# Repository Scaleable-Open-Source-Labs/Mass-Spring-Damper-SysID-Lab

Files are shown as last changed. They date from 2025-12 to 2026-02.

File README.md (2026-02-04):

This is the source repo for the Mass Spring Damper SysID Lab - if you are looking for usage instructions, head to the [user-guide](https://scaleable-open-source-labs.github.io/mass-spring-damper-sysid-lab.html)

---

A low-cost dynamics lab that allows students to perform System Identification on a real Mass-Spring-Damper system.

*Designed by Michael Ruppe for Monash University in partnership with MathWorks®*

## Bill of Materials

### Mechanical Components
- 12 x [SC M3X8 304](https://nhtb.com.au/SC%20M3X8%20304.html)
-  2 x [SC M3X16 304](https://nhtb.com.au/SC%20M3X16%20304.html)
-  2 x [Steel Extension Spring, 27.2 mm x 4 mm OD](https://au.rs-online.com/web/p/extension-springs/0751663)

### Enclosure & Printed Parts
*The printed case and acrylic lid were modeled in OnShape. You can inspect and fork your own copy of the [OnShape project](https://cad.onshape.com/documents/9c2f20cdbdc0ad1f01a0b817/w/781d57bc81f27fd7521e8d8c/e/460a2fa13b5ff0fbf298da99?renderMode=0&uiState=6969b017818b6df756886df9)*

- Case
- Guide Rails
- Lid

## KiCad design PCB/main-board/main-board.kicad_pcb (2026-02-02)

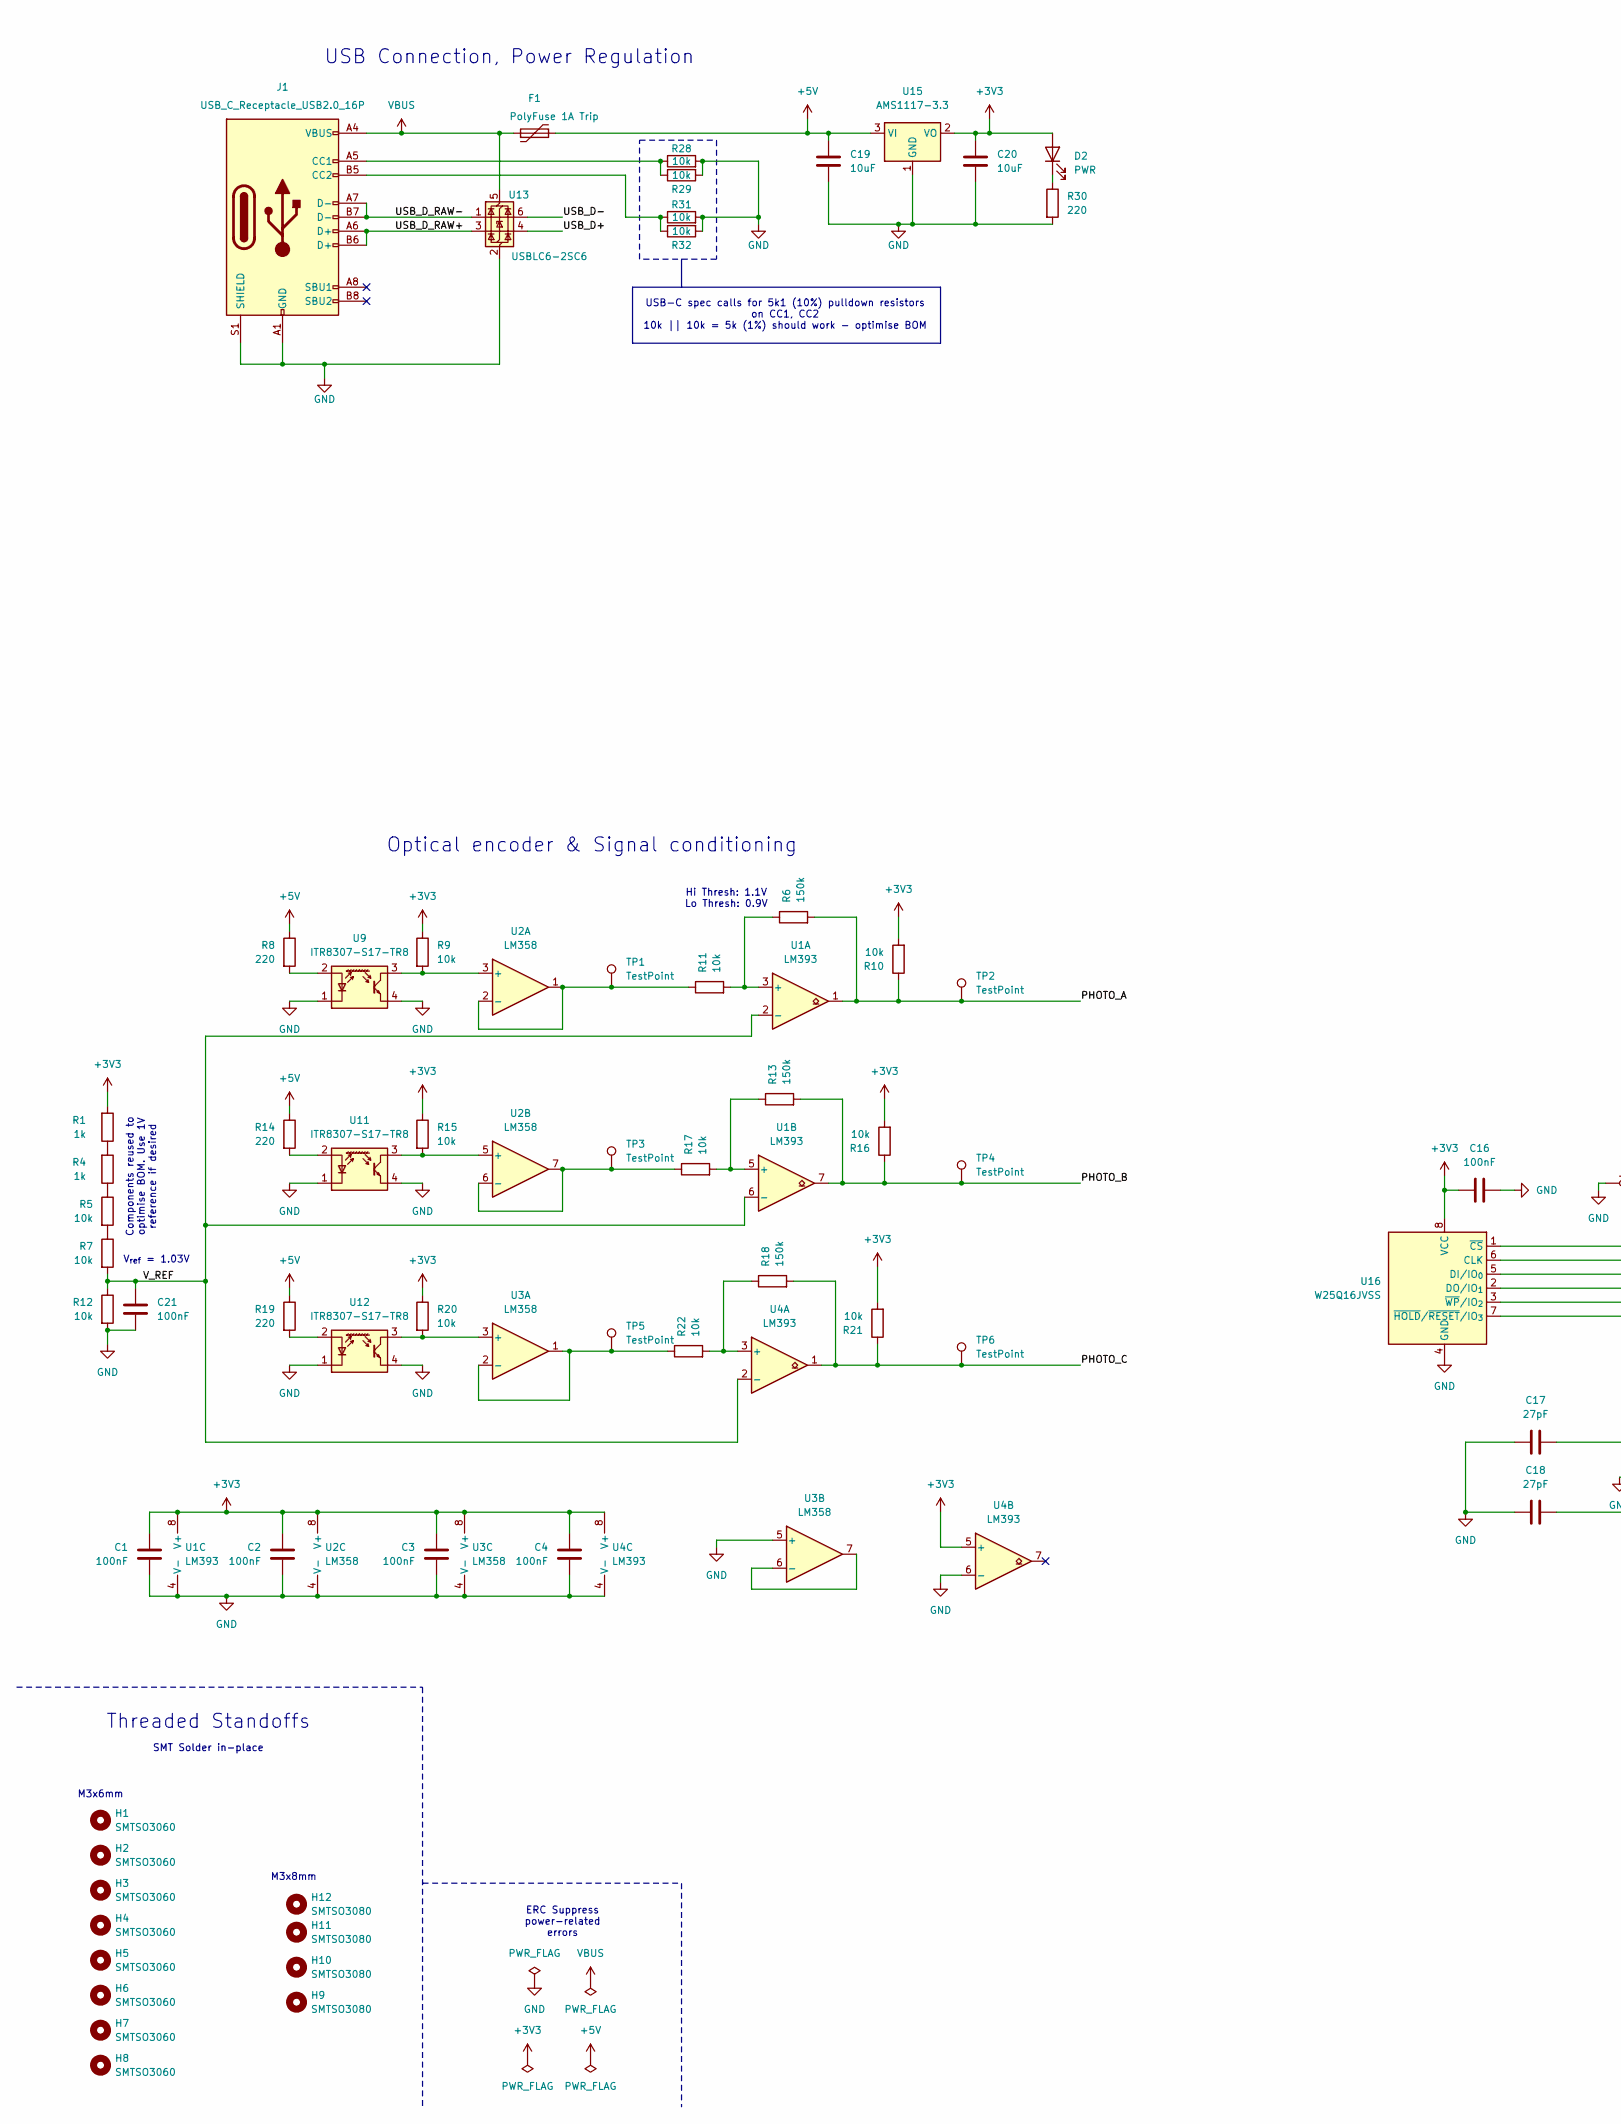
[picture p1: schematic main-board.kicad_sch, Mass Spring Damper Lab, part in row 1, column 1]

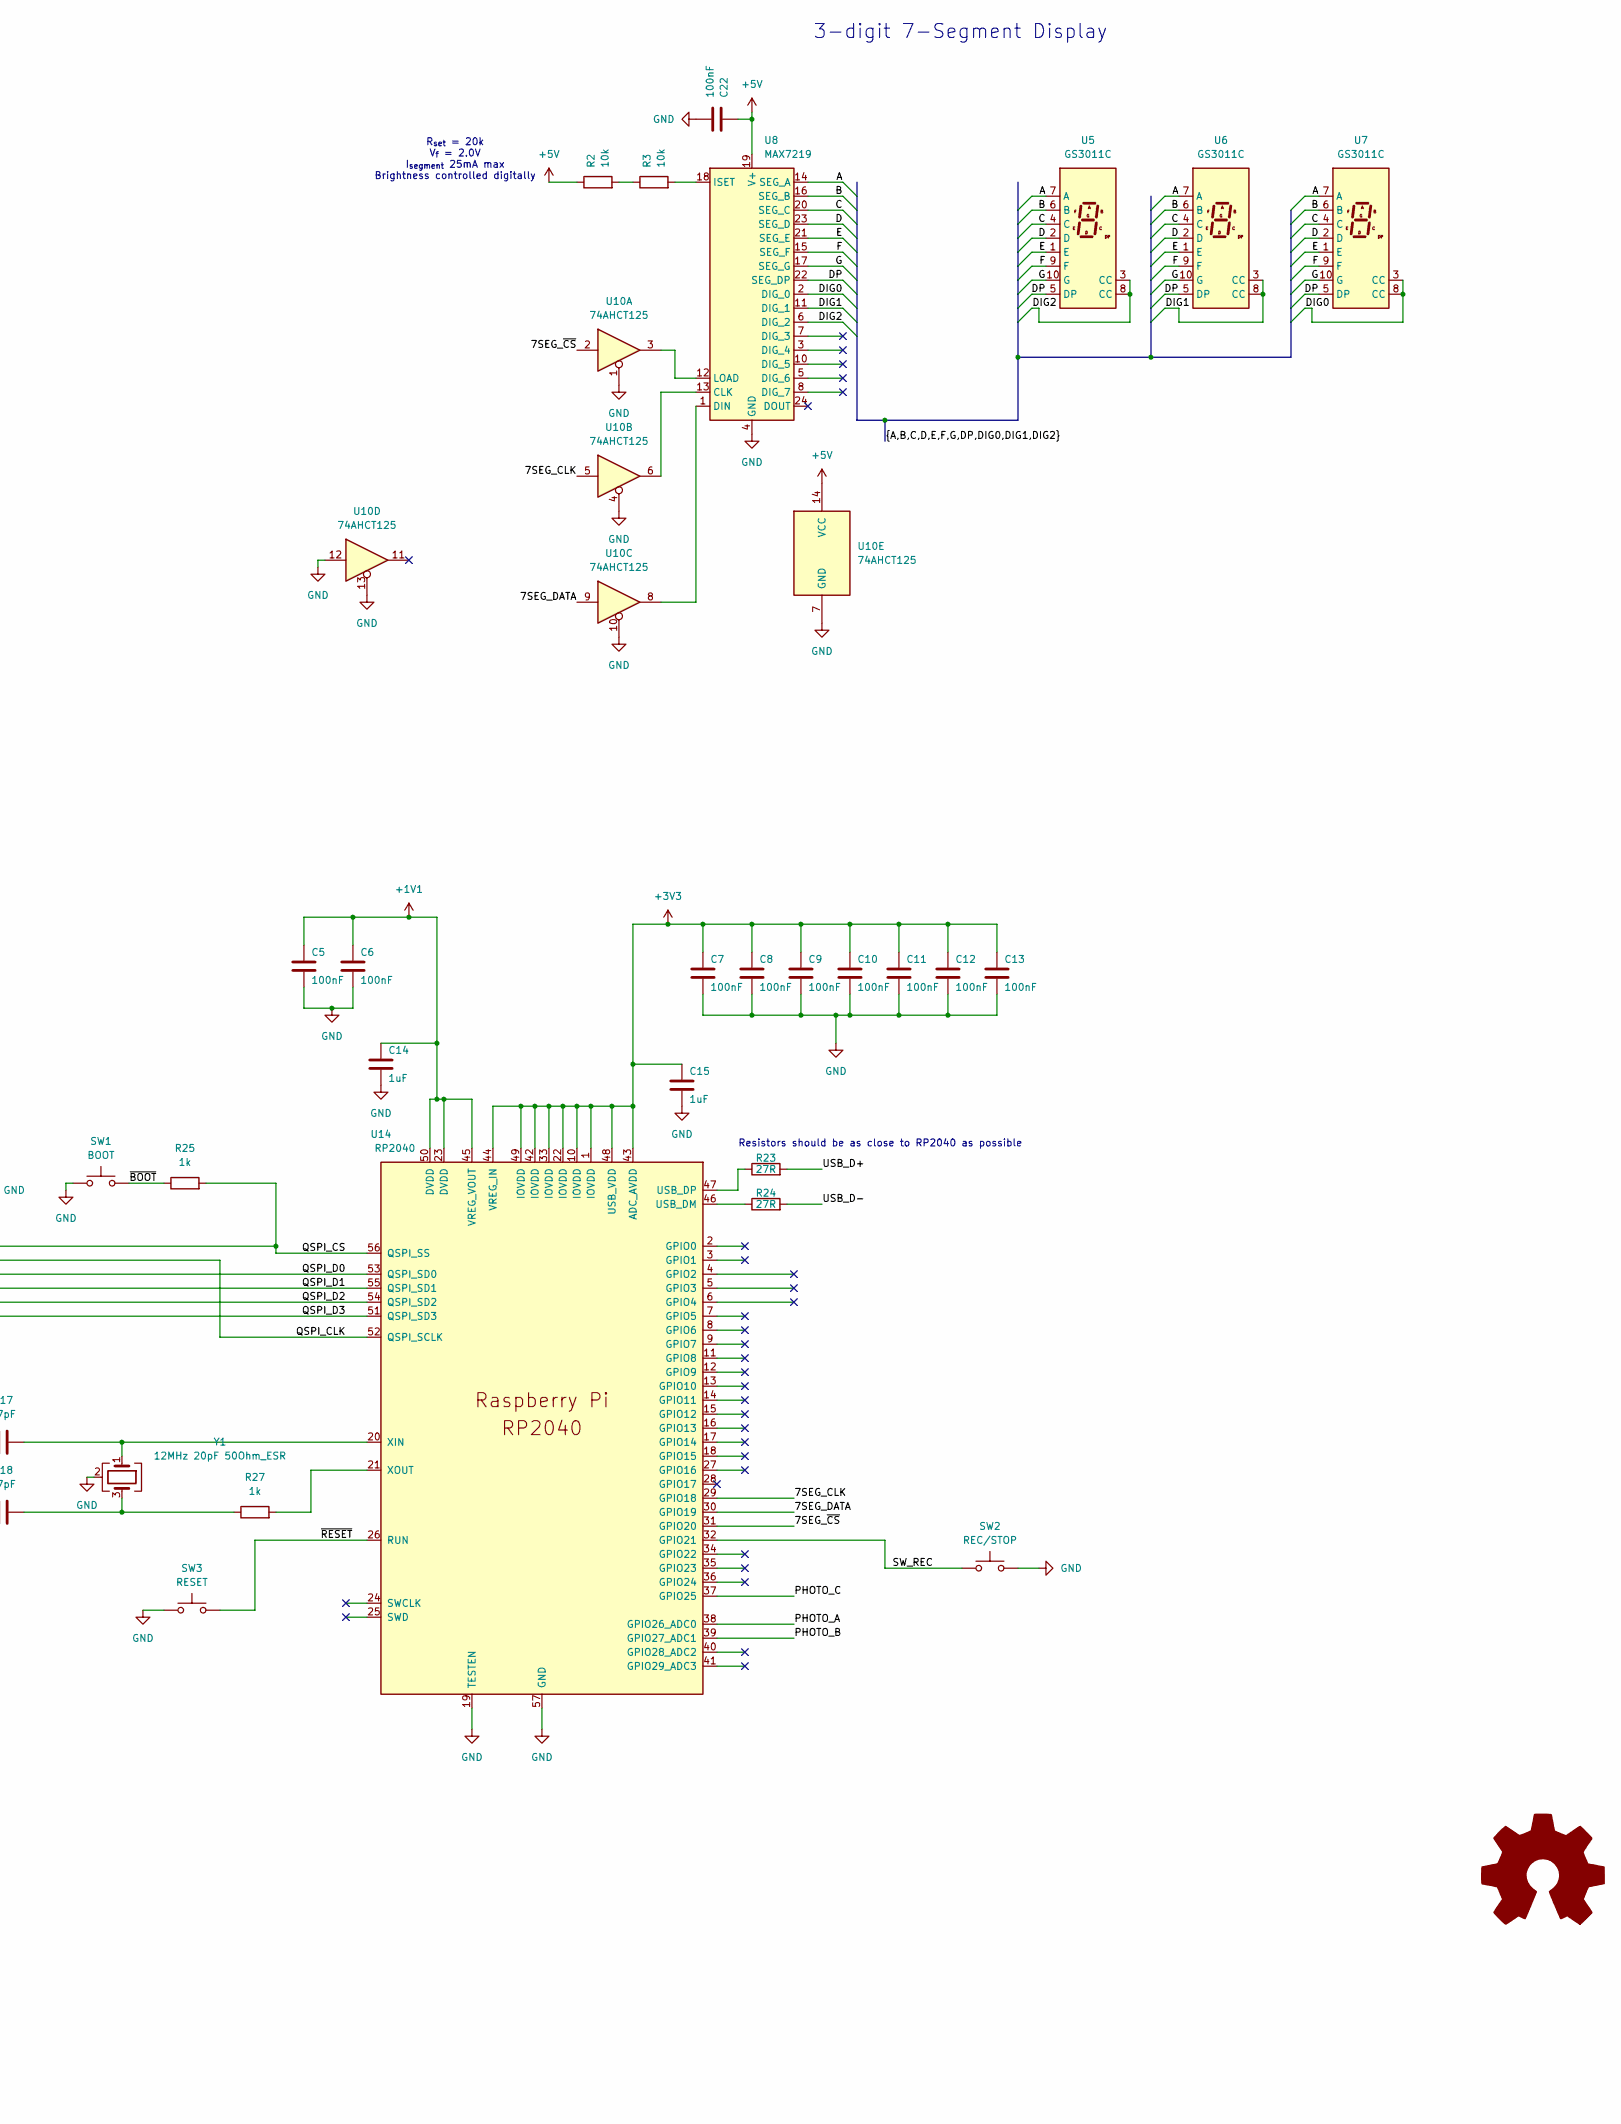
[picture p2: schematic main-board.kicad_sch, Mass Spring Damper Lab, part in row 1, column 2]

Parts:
C1, C2, C3, C4, C5, C6, C7, C8, C9, C10, C11, C12, C13, C16, C21, C22: 100nF; C_0603_1608Metric; LCSC Part # C14663
C14, C15: 1uF; C_0603_1608Metric; LCSC Part # C15849
C17, C18: 27pF; C_0603_1608Metric; LCSC Part # C1656
C19, C20: 10uF; C_0603_1608Metric; LCSC Part # C19702
D2: PWR; LED_0603_1608Metric; LCSC Part # C965807
F1: PolyFuse 1A Trip; R_1206_3216Metric; LCSC Part # C720075
H1, H2, H3, H4, H5, H6, H7, H8: SMTSO3060; MountingHole_SMTSO3060_3.2mm_M3; LCSC Part # C2915637
H9, H10, H11, H12: SMTSO3080; MountingHole_SMTSO3080_3.2mm_M3; LCSC Part # C2916369
J1: USB_C_Receptacle_USB2.0_16P; USB_C_Receptacle_HCTL_HC-TYPE-C-16P-01A; LCSC Part # C2894897
R1, R4, R25, R27: 1k; R_0603_1608Metric; LCSC Part # C21190
R2, R3, R5, R7, R9, R10, R11, R12, R15, R16, R17, R20, R21, R22, R28, R29, R31, R32: 10k; R_0603_1608Metric; LCSC Part # C25804
R6, R13, R18: 150k; R_0603_1608Metric; LCSC Part # C22807
R8, R14, R19, R30: 220; R_0603_1608Metric; LCSC Part # C22962
R23, R24: 27R; R_0603_1608Metric; LCSC Part # C25190
SW1: BOOT; SW_Push_1P1T_NO_E-Switch_TL3301NxxxxxG; LCSC Part # C455109
SW2: REC/STOP; SW_SPST_Omron_B3F-40xx; LCSC Part # C84931
SW3: RESET; SW_SPST_Omron_B3F-40xx; LCSC Part # C84931
TP1, TP2, TP3, TP4, TP5, TP6: TestPoint; TestPoint_Pad_D1.5mm
U1, U4: LM393; SOIC-8_3.9x4.9mm_P1.27mm; LCSC Part # C32901
U2, U3: LM358; SOIC-8_3.9x4.9mm_P1.27mm; LCSC Part # C9418
U5, U6, U7: GS3011C; GS3011; LCSC Part # C22462660
U8: MAX7219; SOIC-24W_7.5x15.4mm_P1.27mm; LCSC Part # C49443603
U9, U11, U12: ITR8307-S17-TR8; Everlight_ITR1201SR10AR; LCSC Part # C81632
U10: 74AHCT125; SOIC-14_3.9x8.7mm_P1.27mm; LCSC Part # C5962
U13: USBLC6-2SC6; SOT-23-6; LCSC Part # C2687116
U14: RP2040; RP2040-QFN-56; PARTREV 1.6.1; LCSC Part # C2040
U15: AMS1117-3.3; SOT-223-3_TabPin2; LCSC Part # C6186
U16: W25Q16JVSS; SOIC-8_5.3x5.3mm_P1.27mm; LCSC Part # C82317
Y1: 12MHz 20pF 50Ohm_ESR; Crystal_SMD_3225-4Pin_3.2x2.5mm; LCSC Part # C133334

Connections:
+1V1: C5.1, C6.1, C14.1, U14.23 (DVDD), U14.45 (VREG_VOUT), U14.50 (DVDD)
+3V3: C1.1, C2.1, C3.1, C4.1, C7.1, C8.1, C9.1, C10.1, C11.1, C12.1, C13.1, C15.1, C16.1, C20.1, D2.2 (A), R1.2, R9.1, R10.2, R15.1, R16.2, R20.1, R21.2, U1.8 (V+), U2.8 (V+), U3.8 (V+), U4.5 (+), U4.8 (V+), U14.1 (IOVDD), U14.10 (IOVDD), U14.22 (IOVDD), U14.33 (IOVDD), U14.42 (IOVDD), U14.43 (ADC_AVDD), U14.44 (VREG_IN), U14.48 (USB_VDD), U14.49 (IOVDD), U15.2 (VO), U16.8 (VCC)
+5V: C19.1, C22.1, F1.2, R2.1, R8.1, R14.1, R19.1, U8.19 (V+), U10.14 (VCC), U15.3 (VI)
/7SEG_CLK: U10.5, U14.29 (GPIO18)
/7SEG_DATA: U10.9, U14.30 (GPIO19)
/7SEG_~CS: U10.2, U14.31 (GPIO20)
/A: U5.7 (A), U6.7 (A), U7.7 (A), U8.14 (SEG_A)
/B: U5.6 (B), U6.6 (B), U7.6 (B), U8.16 (SEG_B)
/C: U5.4 (C), U6.4 (C), U7.4 (C), U8.20 (SEG_C)
/D: U5.2 (D), U6.2 (D), U7.2 (D), U8.23 (SEG_D)
/DIG0: U7.3 (CC), U7.8 (CC), U8.2 (DIG_0)
/DIG1: U6.3 (CC), U6.8 (CC), U8.11 (DIG_1)
/DIG2: U5.3 (CC), U5.8 (CC), U8.6 (DIG_2)
/DP: U5.5 (DP), U6.5 (DP), U7.5 (DP), U8.22 (SEG_DP)
/E: U5.1 (E), U6.1 (E), U7.1 (E), U8.21 (SEG_E)
/F: U5.9 (F), U6.9 (F), U7.9 (F), U8.15 (SEG_F)
/G: U5.10 (G), U6.10 (G), U7.10 (G), U8.17 (SEG_G)
/PHOTO_A: R6.2, R10.1, TP2.1, U1.1, U14.38 (GPIO26_ADC0)
/PHOTO_B: R13.2, R16.1, TP4.1, U1.7, U14.39 (GPIO27_ADC1)
/PHOTO_C: R18.2, R21.1, TP6.1, U4.1, U14.37 (GPIO25)
/QSPI_CLK: U14.52 (QSPI_SCLK), U16.6 (CLK)
/QSPI_CS: R25.2, U14.56 (QSPI_SS), U16.1 (~CS)
/QSPI_D0: U14.53 (QSPI_SD0), U16.5 (DI/IO_{0})
/QSPI_D1: U14.55 (QSPI_SD1), U16.2 (DO/IO_{1})
/QSPI_D2: U14.54 (QSPI_SD2), U16.3 (~WP/IO_{2})
/QSPI_D3: U14.51 (QSPI_SD3), U16.7 (~HOLD/~RESET/IO_{3})
/SW_REC: SW2.1, U14.32 (GPIO21)
/USB_D+: R23.2, U13.4 (I/O2)
/USB_D-: R24.2, U13.6 (I/O1)
/USB_D_RAW+: J1.A6 (D+), J1.B6 (D+), U13.3 (I/O2)
/USB_D_RAW-: J1.A7 (D-), J1.B7 (D-), U13.1 (I/O1)
/V_REF: C21.1, R7.2, R12.1, U1.2 (-), U1.6 (-), U4.2 (-)
/~BOOT: R25.1, SW1.1
/~RESET: SW3.1, U14.26 (RUN)
GND: C1.2, C2.2, C3.2, C4.2, C5.2, C6.2, C7.2, C8.2, C9.2, C10.2, C11.2, C12.2, C13.2, C14.2, C15.2, C16.2, C17.1, C18.1, C19.2, C20.2, C21.2, C22.2, J1.A1 (GND), J1.A12 (GND), J1.B1 (GND), J1.B12 (GND), J1.S1 (SHIELD), R12.2, R28.2, R29.2, R30.2, R31.2, R32.2, SW1.2, SW2.2, SW3.2, U1.4 (V-), U2.4 (V-), U3.4 (V-), U3.5 (+), U4.4 (V-), U4.6 (-), U8.4 (GND), U8.9 (GND), U9.1 (K), U9.4, U10.1, U10.4, U10.7 (GND), U10.10, U10.12, U10.13, U11.1 (K), U11.4, U12.1 (K), U12.4, U13.2 (GND), U14.19 (TESTEN), U14.57 (GND), U15.1 (GND), U16.4 (GND), Y1.2 (G), Y1.4 (G)
unnamed: C18.2, R27.1, Y1.3
unnamed: D2.1 (K), R30.1
unnamed: J1.A5 (CC1), R28.1, R29.1
unnamed: J1.B5 (CC2), R31.1, R32.1
unnamed: R1.1, R4.2
unnamed: R2.2, R3.1
unnamed: R4.1, R5.1
unnamed: R5.2, R7.1
unnamed: R6.1, R11.2, U1.3 (+)
unnamed: R13.1, R17.2, U1.5 (+)
unnamed: R9.2, U2.3 (+), U9.3
unnamed: R11.1, TP1.1, U2.1, U2.2 (-)
unnamed: R15.2, U2.5 (+), U11.3
unnamed: R17.1, TP3.1, U2.6 (-), U2.7
unnamed: R20.2, U3.3 (+), U12.3
unnamed: R22.1, TP5.1, U3.1, U3.2 (-)
unnamed: U3.6 (-), U3.7
unnamed: R18.1, R22.2, U4.3 (+)
unnamed: U8.13 (CLK), U10.6
unnamed: U8.1 (DIN), U10.8
unnamed: R3.2, U8.18 (ISET)
unnamed: U8.12 (LOAD), U10.3
unnamed: R8.2, U9.2 (A)
unnamed: R14.2, U11.2 (A)
unnamed: R19.2, U12.2 (A)
unnamed: R24.1, U14.46 (USB_DM)
unnamed: R23.1, U14.47 (USB_DP)
unnamed: C17.2, U14.20 (XIN), Y1.1
unnamed: R27.2, U14.21 (XOUT)
VBUS: F1.1, J1.A4 (VBUS), J1.A9 (VBUS), J1.B4 (VBUS), J1.B9 (VBUS), U13.5 (VBUS)

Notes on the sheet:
USB-C spec calls for 5k1 (10%) pulldown resistors on CC1, CC2 10k || 10k = 5k (1%) should work - optimise BOM
M3x6mm
Resistors should be as close to RP2040 as possible
Hi Thresh: 1.1V Lo Thresh: 0.9V
3-digit 7-Segment Display
Threaded Standoffs
Components reused to optimise BOM. Use 1V reference if desired
USB Connection, Power Regulation
ERC Suppress power-related errors
SMT Solder in-place
R_{set} = 20k V_{f} = 2.0V I_{segment} 25mA max Brightness controlled digitally
Optical encoder & Signal conditioning
M3x8mm
V_{ref} = 1.03V

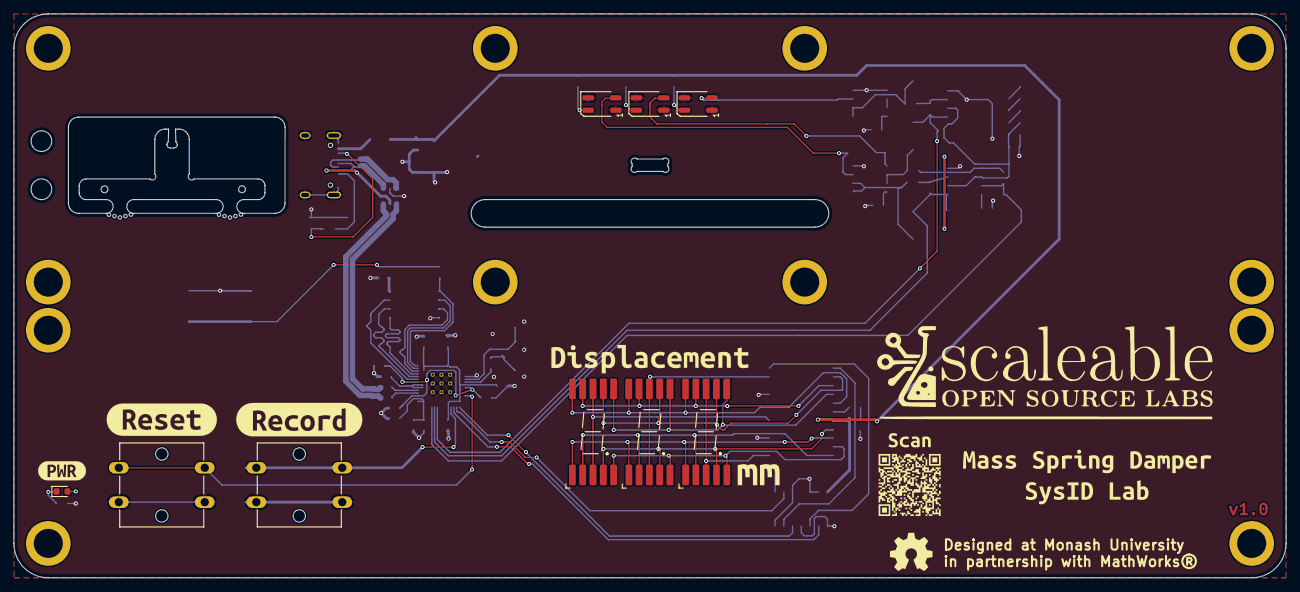
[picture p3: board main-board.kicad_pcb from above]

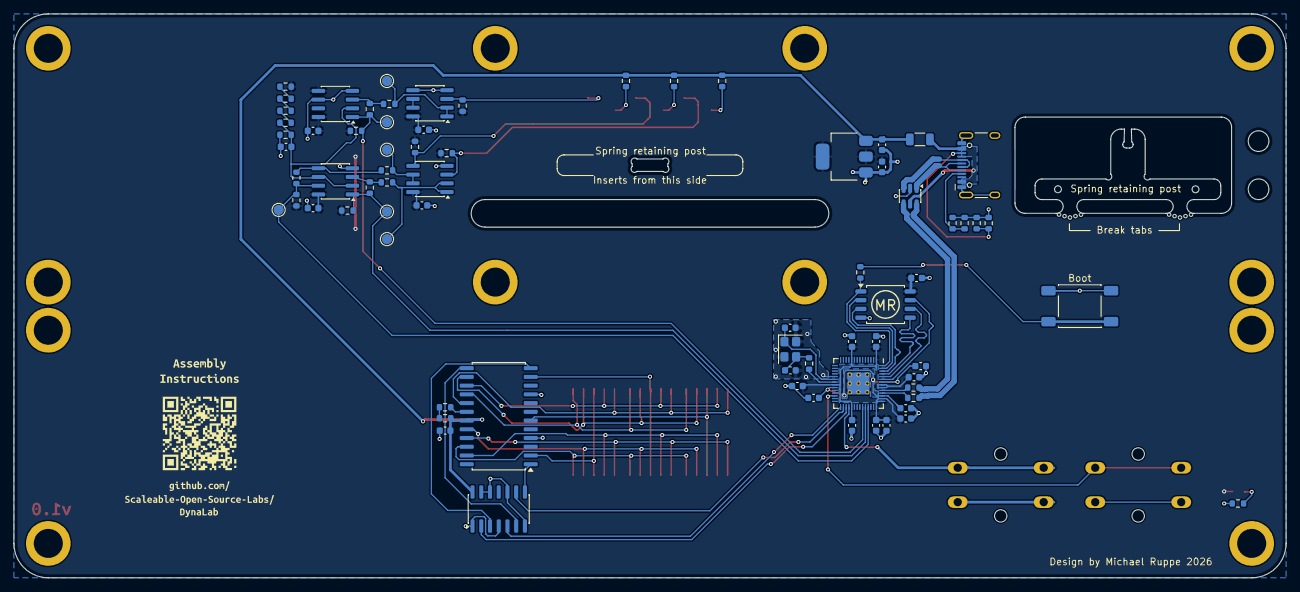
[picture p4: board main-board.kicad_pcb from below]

Board: 2 copper layers, 185.0 x 82.0 mm, 110 parts (86 on the bottom side), 65 nets.

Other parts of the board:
kibuzzard-6930AF86: G***; kibuzzard-6930AF86
kibuzzard-6930AFAB: G***; kibuzzard-6930AFAB
kibuzzard-69645CED: G***; kibuzzard-69645CED
kibuzzard-697836DA: G***; kibuzzard-697836DA
kibuzzard-697848C9: G***; kibuzzard-697848C9
kibuzzard-6964435B: G***; kibuzzard-6964435B
kibuzzard-6978203B: G***; kibuzzard-6978203B
kibuzzard-6978204E: G***; kibuzzard-6978204E
kibuzzard-6978363D: G***; kibuzzard-6978363D
kibuzzard-6978422B: G***; kibuzzard-6978422B
kibuzzard-69310180: G***; kibuzzard-69310180
kibuzzard-69310240: G***; kibuzzard-69310240
kibuzzard-69783696: G***; kibuzzard-69783696
kibuzzard-69784254: G***; kibuzzard-69784254
mousebite1, mousebite2: VAL**; mouse-bite-2mm-4mm-single-sided

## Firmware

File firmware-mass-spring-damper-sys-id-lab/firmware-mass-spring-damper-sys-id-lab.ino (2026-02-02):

#define VERSION_MAJOR 0
#define VERSION_MINOR 1

// Create version string using preprocessor stringification
#define STRINGIFY(x) #x
#define TOSTRING(x) STRINGIFY(x)
#define VERSION_STRING TOSTRING(VERSION_MAJOR) "." TOSTRING(VERSION_MINOR)

#include <Arduino.h>
#include "Adafruit_TinyUSB.h"
#include "ramdisk.h"
#include "gpio.h"
#include "LedControl.h"

LedControl lc = LedControl(19, 18, 20, 1);

#define CAPTURE_TIMEOUT_MS 5000  // maximum possible recording duration
#define MOTION_TIMEOUT_MS 500    // timeout when mass has stopped moving
#define USB_DETACH_DELAY_MS 10
#define SERIAL_WAIT_MS 100
#define POST_CAPTURE_DELAY_MS 1000

// Volatile variables shared between ISR and main loop
volatile bool stateChanged = false;
volatile int positionCounter = 0;

// State tracking
uint8_t currentState = 0;
uint8_t previousState = 0;

unsigned long timestamp = 0;

Adafruit_USBD_MSC usb_msc;

// Data collection structure
#define MAX_DATAPOINTS 5000
struct DataPoint {
  uint32_t millisecond;
  int displacement_mm;
};

DataPoint timeseries[MAX_DATAPOINTS];
int datapoint_count = 0;

// Function to add datapoint
void addDataPoint(uint32_t ms, int disp) {
  if (datapoint_count < MAX_DATAPOINTS) {
    timeseries[datapoint_count].millisecond = ms;
    timeseries[datapoint_count].displacement_mm = disp;
    datapoint_count++;
  }
}


// Generate CSV content from timeseries data
void generateCSV() {
  uint32_t current_block = 4;  // Data blocks start at block 4 (Block0: Boot, Block1: FAT1, Block2: FAT2, Block3: Root Dir)
  uint32_t block_offset = 0;
  char line_buffer[20];  // Single line buffer

  // Write header
  uint32_t len = sprintf(line_buffer, "Time [us],Displacement [mm]\n");
  writeToBlocks(line_buffer, len, current_block, block_offset);

  // Write data rows
  for (int i = 0; i < datapoint_count; i++) {
    len = sprintf(line_buffer, "%lu,%d\n",
                  timeseries[i].millisecond,
                  timeseries[i].displacement_mm);
    writeToBlocks(line_buffer, len, current_block, block_offset);
  }

  // Calculate file metrics
  uint32_t file_size = (current_block - 4) * DISK_BLOCK_SIZE + block_offset;
  uint32_t blocks_needed = current_block - 4 + (block_offset > 0 ? 1 : 0);

  // Zero remainder of final block. Partial blocks must be zeroed to avoid garbage data.
  if (block_offset > 0) {
    memset(msc_disk[current_block] + block_offset, 0, DISK_BLOCK_SIZE - block_offset);
  }

  // Update BOTH FAT Tables (Windows requires both copies to match)
  for (int fat_copy = 0; fat_copy < 2; fat_copy++) {
    uint8_t* fat = msc_disk[1 + fat_copy];  // Block 1 (FAT1) and Block 2 (FAT2)

    // Chain logic:
    // if not last block: next_cluster = cluster + 1 (points to next block)
    // if last block: next_cluster = 0xFFF (EOF marker)
    for (uint32_t cluster = 2; cluster < 2 + blocks_needed; cluster++) {
      uint16_t next_cluster = (cluster < 2 + blocks_needed - 1) ? (cluster + 1) : 0xFFF;
      uint32_t byte_offset = (cluster * 3) / 2;

      // FAT12 Packing (12 bits per entry). Two entries = 3 bytes.
      if (cluster % 2 == 0) {
        fat[byte_offset] = next_cluster & 0xFF;
        fat[byte_offset + 1] = (fat[byte_offset + 1] & 0xF0) | ((next_cluster >> 8) & 0x0F);
      } else {
        fat[byte_offset] = (fat[byte_offset] & 0x0F) | ((next_cluster << 4) & 0xF0);
        fat[byte_offset + 1] = (next_cluster >> 4) & 0xFF;
      }
    }
  }

// Update Block3 directory entry
// Block3, starting byte 32 defines Data_.csv
// Bytes 37-39: Characters 6-8 of filename (Data_###) - generate three random alphanumeric characters to append to this file (helps avoid file-overwrites when user copies data onto PC)
// Bytes 60-63: 4-bytes little-endian file size
#define ROOT_DIR_BLOCK 3
#define FILENAME_RANDOM_OFFSET 37  // Start of the 3 spaces in "DATA_   "
#define FILE_SIZE_OFFSET 60

  // Generate 3 random alphanumeric characters
  const char charset[] = "ABCDEFGHIJKLMNOPQRSTUVWXYZ0123456789";
  const int charset_size = sizeof(charset) - 1;  // Exclude null terminator
  randomSeed(micros());
  for (int i = 0; i < 3; i++) {
    msc_disk[ROOT_DIR_BLOCK][FILENAME_RANDOM_OFFSET + i] = charset[random(charset_size)];
  }

  // Update file size
  msc_disk[ROOT_DIR_BLOCK][FILE_SIZE_OFFSET] = file_size & 0xFF;
  msc_disk[ROOT_DIR_BLOCK][FILE_SIZE_OFFSET + 1] = (file_size >> 8) & 0xFF;
  msc_disk[ROOT_DIR_BLOCK][FILE_SIZE_OFFSET + 2] = (file_size >> 16) & 0xFF;
  msc_disk[ROOT_DIR_BLOCK][FILE_SIZE_OFFSET + 3] = (file_size >> 24) & 0xFF;
}

static void writeToBlocks(const char* data, uint32_t len,
                          uint32_t& current_block, uint32_t& block_offset) {
  for (uint32_t i = 0; i < len; i++) {
    msc_disk[current_block][block_offset++] = data[i];
    if (block_offset >= DISK_BLOCK_SIZE) {
      current_block++;
      block_offset = 0;
    }
  }
}

void updateBootSectorForDiskSize() {
  // Update total sectors in boot sector (bytes 19-20)
  msc_disk[0][19] = DISK_BLOCK_NUM & 0xFF;
  msc_disk[0][20] = (DISK_BLOCK_NUM >> 8) & 0xFF;

  // Calculate required FAT size (12 bits per entry, 8 entries per 3 bytes)
  uint32_t fat_entries = DISK_BLOCK_NUM + 2;  // +2 for reserved entries
  uint32_t fat_bytes = (fat_entries * 3 + 1) / 2;
  uint32_t sectors_per_fat = (fat_bytes + DISK_BLOCK_SIZE - 1) / DISK_BLOCK_SIZE;

  // Update sectors per FAT (bytes 22-23)
  msc_disk[0][22] = sectors_per_fat & 0xFF;
  msc_disk[0][23] = (sectors_per_fat >> 8) & 0xFF;
}


enum modes {
  INITIALISED,
  STANDBY,
  CAPTURE,
  MOUNT_DRIVE
};
modes mode = STANDBY;
modes last_mode = INITIALISED;

// the setup function runs once when you press reset or power the board
void setup() {
  // Manual begin() is required on core without built-in support e.g. mbed rp2040
  if (!TinyUSBDevice.isInitialized()) {
    TinyUSBDevice.begin(0);
  }

  Serial.begin(115200);
  static uint8_t serial_initialiser_counter = 0;
  while (!Serial && serial_initialiser_counter < 5) {
    delay(100);
    serial_initialiser_counter++;
  }

  gpio_initialise();

  // Set disk vendor id, product id and revision with string up to 8, 16, 4 characters respectively
  usb_msc.setID("DntPanic", "Mass Storage", VERSION_STRING);

  // Set disk size
  usb_msc.setCapacity(DISK_BLOCK_NUM, DISK_BLOCK_SIZE);
  updateBootSectorForDiskSize();
  // Set callback
  usb_msc.setReadWriteCallback(msc_read_callback, msc_write_callback, msc_flush_callback);
  usb_msc.setStartStopCallback(msc_start_stop_callback);
  usb_msc.setReadyCallback(msc_ready_callback);

  // Set Lun ready (RAM disk is always ready)
  usb_msc.setUnitReady(true);

  // 7-segment display
  lc.shutdown(0, false);  // wakeup
  lc.setIntensity(0, 15);  // max brightness (0 to 15)
  lc.clearDisplay(0);

}



void loop() {
  switch (mode) {
    case STANDBY:
      handleStandbyMode();
      break;
    case CAPTURE:
      handleCaptureMode();
      break;
    case MOUNT_DRIVE:
      handleMountDriveMode();
      break;
  }
}


void handleStandbyMode() {
  if (mode != last_mode) {
    Serial.println("Standing By");

    enableEncoderInterrupts();


    last_mode = mode;

    // throw away first reading - zeros the device and updates encoder-last-state
    processEncoderChange();
    positionCounter = 0;
  }
  if (digitalRead(btnRec) == 0) mode = CAPTURE;

  // Display live displacement
  processEncoderChange();
  long units = abs(positionCounter) % 10;
  long tens = (abs(positionCounter) / 10) % 10;
  lc.setDigit(0, 0, units, false);
  if (tens != 0) lc.setDigit(0, 1, tens, false);
  else lc.setChar(0, 1, ' ', false);

  if (positionCounter < 0) lc.setChar(0, 2, '-', false);
  else lc.setChar(0, 2, ' ', false);
}

void handleCaptureMode() {
  static unsigned long time_begin;
  static unsigned int num_points = 0;

  // Mode entry
  if (mode != last_mode) {
    Serial.println("Capturing");
    digitalWrite(ledRec, HIGH);

    // display "rEC" (recording)
    lc.setRow(0, 2, 0x05);         // r
    lc.setChar(0, 1, 'E', false);  // E
    lc.setRow(0, 0, 0x4E);         // c
    last_mode = mode;

    stateChanged = false;
    time_begin = micros();
  }
  static unsigned long lastMotion = 0;
  // Process state changes
  if (stateChanged) {
    num_points++;

    stateChanged = false;
    processEncoderChange();
    if (num_points == 1) time_begin = timestamp;  // first timestamp starts at zero

    lastMotion = millis();

    if (num_points > MAX_DATAPOINTS) {
      mode = MOUNT_DRIVE;
      return;
    }

    addDataPoint(timestamp - time_begin, positionCounter);
    Serial.printf("%8d, %4d\n", timestamp, positionCounter);
  }


  // Timeout check

  bool motionTimeout = (millis() - lastMotion > MOTION_TIMEOUT_MS) && num_points > 100;

  if (micros() - time_begin > 1000 * CAPTURE_TIMEOUT_MS || motionTimeout) {
    disableEncoderInterrupts();
    Serial.println("Done");
    digitalWrite(ledRec, LOW);
    mode = MOUNT_DRIVE;
  }
}

void handleMountDriveMode() {
  if (mode != last_mode) {
    last_mode = MOUNT_DRIVE;

    // Display 'U.S.b.' on 7-seg with decimal points
    lc.setRow(0, 2, 0x3E | 0x80);         // U.
    lc.setDigit(0, 1, 5, true);           // S.
    lc.setChar(0, 0, 'b', true);          // b.

    generateCSV();
    usb_msc.begin();

    if (TinyUSBDevice.mounted()) {
      TinyUSBDevice.detach();
      delay(1000);  // Longer delay for Windows to forget the device
      TinyUSBDevice.attach();
    }
  }

#ifdef TINYUSB_NEED_POLLING_TASK
  TinyUSBDevice.task();
#endif
}



void encoderISR() {
  timestamp = micros();
  stateChanged = true;
}

// Process encoder state change and update position
void processEncoderChange() {
  currentState = readEncoderState();
  // Only process if state actually changed
  if (currentState != previousState) {
    int direction = getDirection(previousState, currentState);

    if (direction != 0) {
      // Disable interrupts briefly while updating position
      noInterrupts();
      positionCounter += direction;
      interrupts();
    }

    previousState = currentState;
  }
}

// Encoder state transition lookup table
// each state is encoded by the 3-bit value of the optical sensors.
// Index: [previous_state][current_state] -> direction
// Returns: +1 forward, -1 reverse, 0 invalid/no-change
const int8_t ENCODER_TRANSITION_TABLE[8][8] = {
  { 0, -1, 0, 0, 1, 0, 0, 0 },  // 0 (0b000) previous
  { 1, 0, 0, -1, 0, 0, 0, 0 },  // 1 (0b001)
  { 0, 0, 0, 0, 0, 0, 0, 0 },   // 2 (0b010) invalid
  { 0, 1, 0, 0, 0, 0, 0, -1 },  // 3 (0b011)
  { -1, 0, 0, 0, 0, 0, 1, 0 },  // 4 (0b100)
  { 0, 0, 0, 0, 0, 0, 0, 0 },   // 5 (0b101) invalid
  { 0, 0, 0, 0, -1, 0, 0, 1 },  // 6 (0b110)
  { 0, 0, 0, 1, 0, 0, -1, 0 },  // 7 (0b111)
};

// Simplified direction function - single lookup, no searching
int getDirection(uint8_t prevState, uint8_t currState) {
  // Bounds check for safety
  if (prevState > 7 || currState > 7) return 0;

  return ENCODER_TRANSITION_TABLE[prevState][currState];
}


// Callback invoked when received READ10 command.
// Copy disk's data to buffer (up to bufsize) and
// return number of copied bytes (must be multiple of block size)
int32_t msc_read_callback(uint32_t lba, void* buffer, uint32_t bufsize) {
  uint8_t const* addr = msc_disk[lba];
  memcpy(buffer, addr, bufsize);

  return bufsize;
}

// Callback invoked when received WRITE10 command.
// Process data in buffer to disk's storage and
// return number of written bytes (must be multiple of block size)
int32_t msc_write_callback(uint32_t lba, uint8_t* buffer, uint32_t bufsize) {
  uint8_t* addr = msc_disk[lba];
  memcpy(addr, buffer, bufsize);

  return bufsize;
}

// Callback invoked when WRITE10 command is completed (status received and accepted by host).
// used to flush any pending cache.
void msc_flush_callback(void) {
  // nothing to do
}

bool msc_start_stop_callback(uint8_t power_condition, bool start, bool load_eject) {
  Serial.printf("Start/Stop callback: power condition %u, start %u, load_eject %u\n", power_condition, start, load_eject);
  return true;
}
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

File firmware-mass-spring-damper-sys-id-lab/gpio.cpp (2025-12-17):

#include "gpio.h"

void gpio_initialise() {
  pinMode(chA, INPUT);  // Use INPUT to ensure Pull-up/down resistors are disabled - else the signal from the reflectance sensor is corrupted.
  pinMode(chB, INPUT);
  pinMode(chC, INPUT);

  pinMode(btnRec, INPUT_PULLUP);
  pinMode(ledRec, OUTPUT);
}


// Read current encoder state (3-bit value)
uint8_t readEncoderState() {
  uint8_t state = 0;

  // Read pins and construct 3-bit state (A=bit2, B=bit1, C=bit0)
  if (!digitalRead(chA)) state |= 0b100;  // Assuming active LOW sensors
  if (!digitalRead(chB)) state |= 0b010;
  if (!digitalRead(chC)) state |= 0b001;

  return state;
}

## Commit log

2025-12-03 initial commit with WIP PCB and Code
    [028_7seg.stp, DynaLab.kicad_pcb, DynaLab.kicad_sch, ITR8307_S18_TR8_C_.stp]
2025-12-04 v0 routing complete - no errs
    [DynaLab.kicad_pcb, DynaLab.kicad_sch]
2026-01-29 rename main PCB project to "main-board"
    [main-board.kicad_pcb, main-board.kicad_sch]
2026-02-02 update 7seg display (symbol, footprint, 3Dpackage), README
    [main-board.kicad_pcb, main-board.kicad_sch]
